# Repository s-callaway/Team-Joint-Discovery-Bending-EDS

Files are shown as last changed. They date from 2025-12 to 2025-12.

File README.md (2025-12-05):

# Team-Joint-Discovery-Bending-EDS
Repository containing all of the relevant information for Team Joint Discovery's senior design project

## ESP Motor Controller
The file containing "ESP32_motor_controller.ino" is to be used with an ESP32 and A4988 stepper motor driver. The limit switches are not required but are highly encouraged. If limit switches are not used, ensure that homing is defined to be false.

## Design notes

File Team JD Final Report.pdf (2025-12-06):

Team Joint Discovery

Bending Rig for an Electrodynamic Lunar Dust Shielding System

Final Report

ME 4723 – Interdisciplinary Capstone

Dr. Julie Linsey

julie.linsey@me.gatech.edu

Georgia Institute of Technology

Atlanta, GA

Drew Peljovich – ME

Jackson Buley – ME

Sasha Callaway – ECE

Spencer Hopkins – ME

Vikas Muralidharan – MSE

December 5, 2025

i

### Table of Contents

Appendix | A
Budget Appendix | C

ii

### Executive Summary

Lunar dust poses one of the greatest engineering challenges for sustained human presence on the Moon.

Its abrasive, electrostatically charged particles adhere to nearly every surface, degrading materials and

shortening the lifespan of critical systems. To address this, Team Joint Discovery was tasked with

designing a compact, vacuum‑compatible rig to test the bending performance of a flexible

Electrodynamic Dust Shield (EDS) thin‑film, a promising technology for dust mitigation in future lunar

missions.

The design problem centers on creating a repeatable, reliable bending mechanism that operates within the

strict constraints of Georgia Tech’s high‑vacuum chamber. Key technical hurdles include the chamber’s

limited size (6.1‑inch sphere with a 1×1 inch mounting platform) and the need for materials that can

withstand 10⁻⁸ torr without outgassing. The team’s solution leverages one existing and one purchased

linear bellows drive to cyclically bend the EDS film.

The team created structured design tools including a House of Quality, specification sheets, function trees,

morph charts, and evaluation matrices to guide the final product. The team translated stakeholder needs

into measurable engineering requirements. Market research and interviews with GT CLEVER researchers

and space technology experts further shaped the design, ensuring alignment with both research goals and

broader commercialization potential.

The rig’s key performance specifications include compact integration within the chamber, repeatable

bending cycles, and the ability to activate EDS during testing. Proof of concept was demonstrated by

successful cyclic bending of the EDS film in atmospheric conditions. This capability not only validates

the EDS under mechanical stress but also supports its potential use in protecting spacecraft components,

habitats, and instruments in lunar environments.

The final design is outlined in engineering drawings. Next steps for the project before implementation

under high vacuum is to translate these drawings and prototypes made of PLA material into machined

aluminum stock. Additionally, a motorized linear actuator will need to be purchased that is ultra-high

vacuum compatible to perform the bending test itself.

iii

### Nomenclature

Symbol | Meaning
Hz | Frequency, measured in Hertz
V | Voltage, measure in volts
Torr | Pressure, measured in torr

### Glossary

Acronym | Meaning
ASA | American Standards Association
ASTM | American Society for Testing and Materials
EDS | Electro-Dynamic Shielding
EVA | Extravehicular Activity
HOQ | House of Quality
IEC | International Electrotechnical Commission
JD | Joint Discovery

### Introduction

Team Joint Discovery has been tasked with developing a testing rig to repeatably bend a flexible

Electrodynamic Dust Shielding (EDS) thin film in a vacuum chamber. The film is made of a polyethylene

substrate with graphene-oxide channels etched into the substrate to form a conductive electrical grid.

When an alternating current (AC) of low frequency (10 Hz) and high voltage (>600 V) is applied to the

ends of the electrode, the EDS system is “active”, which repels dust from its surface. A visualization is

shown below in figure 1. Typical EDS devices include conducting electrode thin-films (Indium-Tin

Oxide, silver nanowires, etc). The application of these thin films is to attach surfaces that will face

performance issues due to dust collections such as solar panels and thermal radiators. Due to the material

composition of this specific EDS, it can bend and fold around surfaces as opposed to traditional inflexible

designs. This makes it particularly useful for a variety of lunar applications. Possible applications of this

system include shielding retractable/extendable spacecraft components, rovers, astronaut spacesuits from

excessive lunar dust, and on the outside of inflatable lunar habitats to protect from lunar dust kicked up by

human activity nearby.

A testing rig for the EDS system must comply with a set of strict problem

constraints for use in a high vacuum chamber. For one, the vacuum chamber

reaches pressures of 10⁻⁸
torr. As such, any equipment inside the chamber must

be able to withstand the pressure without collapsing in the high vacuum

environment. Additionally, some plastic materials cannot be used in the chamber

due to the off-gassing effects that could negatively affect the efficiency of the

closed system. Moreover, the vacuum chamber has limited mechanical

passthrough and electrical connection availability. The laboratory currently has

one linear bellows drive available for use in the vacuum chamber, and due to the

high cost of such devices it is preferrable to use the in-stock device without

purchasing other systems. There are six electrical connections available, but

under operating conditions with the dust dropper functioning and the EDS

powered, there are only two connections available.

Most importantly, the dimensions of the vacuum chamber present physical

constraints that will significantly impact the design of any internal mechanisms. The central sphere of the

chamber measures 6.1 inches in diameter. Within the central sphere sits a lunar dust hopper mounted to

the top of the chamber (see Figure 1). For mounting purposes, there is a 1inch-by-1inch platform to

Figure 1: Visualization
of EDS device secure the bending rig that will attach to the bottom of the chamber. The testing rig that will be used with

the EDS will have to conform to these size constraints, potentially sacrificing the ability to perform

different types of bending tests with one system.

The desired solution is a compact, vacuum-compatible bending rig capable of repeatable cyclic loading of

the EDS film. Key performance aspects include precise control of bending angle, durability under

vacuum, and integration with the dust hopper system. Proof of concept will be demonstrated by operating

the rig in the chamber with the EDS powered and dust applied, validating dust-repelling performance

under mechanical stress.

Value Statements

Scientific Impact: The proposed testing rig will enable scientists to repeatedly test the Electro-Dynamic

Shielding (EDS) system under realistic bending and dusting conditions, supporting validation of its dust-

repelling capabilities under cyclic loading.

Engineering Impact: The testing rig proposed also improves materials engineering testing in vacuum

conditions, forming design improvements and material selection for space-grade components.

Mission Reliability: Supports development of dust mitigation technologies for lunar rovers, astronaut

suits, and inflatable habitats, reducing downtime and maintenance in harsh lunar environments.

Commercialization Potential: Facilitates proof-of-concept demonstrations that can accelerate

technology readiness levels (TRLs), attract funding, and support patent filings for novel dust mitigation

systems.

This report covers Team JD’s initial problem brainstorming, including an analysis of existing products

(testing standards, patents), analysis of codes and standards, talking with stakeholders to identify their

needs, and the team’s initial designs.

### Existing Products and Prior Art

This section analyzes the current state of the art in lunar dust mitigation, with a focus on Electrodynamic

Dust Shield (EDS) technology. It identifies the gap in the market for a validated, flexible EDS system and

situates the test fixture and experiment plan within this landscape.

Several other dust mitigation strategies have been proposed or tested, but all have significant drawbacks

compared to the EDS. (Gaier, 2007)

Table 1: Existing Lunar Dust Mitigation Strategies/Solutions

Solution | Lunar Dust Mitigation Method | Pros | Cons
Mechanical Wiper/Brush | Physically sweeps dust off a surface | Simple mechanical design, potentially more deterministic | Moving parts than can fail due to presence of lunar dust; movement requires additional mass, power, complexity; ineffective for complex geometries
Compressed Gas Jets | Blows dust via a burst of gas | Simple solution with few moving parts | Consumable resource that is mass intensive; can further contaminate environment with dust redistribution
Passive Coatings | Superhydrophobic or other low-adhesive surfaces to reduce dust attraction | Solid state and simple solution | Not active; can wear down overtime with excessive use; cannot remove accumulated dust

The listed non-EDS solutions establish the clear need for a flexible, solid state, low power, and non-

consumable active cleaning system. This leads to the currently available and existing designs for EDS

systems for lunar dust mitigation.

Patent Search and Related Concepts

A preliminary patent search reveals significant activity in EDS technology, held by Boeing and Boston

University.

a. US12121910B2: “Dust mitigation system utilizing conductive fibers” (Boeing Co.). This patent

describes a flexible fabric like a dust mitigation system. This specific patent does not describe

bending evaluation/performance. It also is focused on using it as a woven fabric which is different

from the solution proposed by the GT CLEVER team.

b. US9433336B2: “Self-cleaning solar panels and concentrators with transparent electrodynamic

screens” (Boston University). This solution is for a firm EDS used to protect solar panels while

still allowing them to harness the sun’s radiation for power. The physical principle of dust

removal remains the same as GT CLEVER’s EDS, but it is not flexible.

The existence of these patents confirms the commercial and scientific value of flexible EDS. This project

does not seek to invent the flexible EDS itself, but to create the critical bending test required to mature

this technology.

A further example of prior art that was found comes from IPC Test Method 2.4.3, which depicts a test set

up that is designed to measure the bending performance of flexible printed circuit boards (Technical

Committees of IPC, 2022). This prior art demonstrates a proven methodology for testing the mechanical

durability of flexible, conductive materials, providing a foundational reference for the EDS-specific test

design.

Relevance and Differentiation for Intended Design

The test fixture and bending experiments are relevant to the prior art as stated before but is still distinct to

be its own project. The focus of this project is to quantify the EDS’ bending as a commercial selling point.

The test fixture will generate the quantitative data (e.g., "cleaning efficiency remains >95% after 1,000

bend cycles to a 5mm radius") required to substantiate this advantage to potential customers like NASA.

There exists no commercial "Flexible EDS Bending Test Fixtures" on the market. The design addresses a

specific, unmet need within the R&D pipeline for this emerging technology.

Existing Testing Systems

There are very few existing test systems that allow cyclic bending of a flexible film inside a vacuum

chamber, particularly in laboratory-scale vacuum systems. Most vacuum test fixtures focus on thermal

cycling, outgassing characterization, or static mechanical loading, not repeated flexing of thin-film

electronics. Because of this, the closest prior art comes from adjacent domains that required similar

mechanical-in-vacuum capabilities.

One of the most relevant examples is a NASA study titled “The Effect of Vacuum on the Fatigue and

Stress-Rupture Properties of S-816 and Inconel 550 at 1500°F.” (Freche, 1965). Although the study

investigated high-temperature fatigue in metallic specimens rather than polymeric films, the mechanical

test architecture is directly applicable to the requirements of a flexible EDS evaluation.

Figure 2: Fatigue Test Apparatus

Although the mechanical scale and material system differ from the thin-film EDS, this NASA apparatus

demonstrates that cyclic bending in vacuum can be achieved using external actuation and vacuum-

mechanical interfaces. The NASA fatigue apparatus serves as architectural precedent but fails to provide

the specific integration of vacuum operation, controlled bending radius, and electrical excitation needed

for flexible EDS validation.

### Codes and Standards

Several codes and standards informed the ideation of the first prototype. Included in this section is a

summary of those codes and their relative importance.

IEC 62899-202-5

IEC standard 62899-202-5 is the most applicable to team JD’s final product. An excerpt from the

introduction highlights the basis for the reason behind this application:

In this document, a mechanical bending test is described to evaluate the electrical property of a printed

conductive layer on a substrate under repeated mechanical deformations. This sliding plate test method

can be available for practical application in the industry by enabling the long-term reliability testing of

printed film. (TC 119 - Printed Electronics, 2018)

The EDS system is very similar to the film described in the standard. A graphene layer is printed on top of

a polymer substrate to repel the lunar dust. Furthermore, it is necessary to repeatedly deform the piece to

understand its resilience to bending. The standard gives clear instructions on how to perform the test, and

the structure of the bending rig itself. When comparing team JD’s ideation to Figure 3, the IEC standard

served as a clear inspiration for the final design.

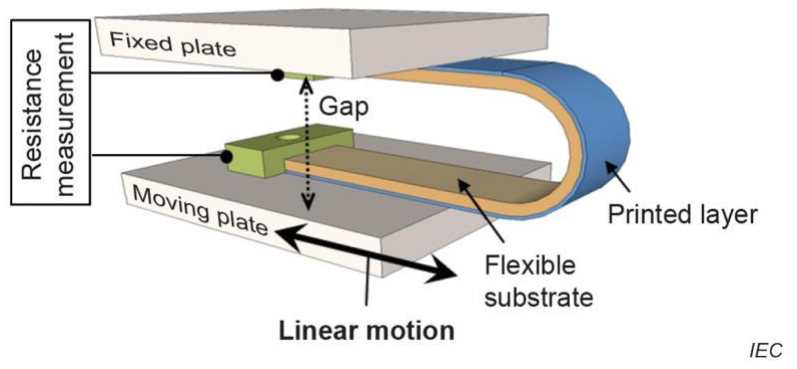
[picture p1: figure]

Figure 3: Schematic diagram of mechanical test of printed film

While not explicitly described, the standard does call out for variable adjustment of the gap between fixed

and moving plates. Team JD will implement this variability in the final design, but not follow the exact

mechanisms described in the standard. The test depicts the horizontal motion of the printed layer by the

moving plate. After speaking with key stakeholders, this will not be possible in the final design.

Therefore, Team JD will have to modify the standard so that it can perform in a vertical position.

Other Applicable Standards

During the ideation phase of the project, Team Joint Discovery found and used several other standards as

a basis for the final project. While not implemented as directly as 62899-202-5, these standards guided the

team towards the end goal and provided inspiration for certain design choices.

The first of the standards considered was ASTM

F392, called Standard Practice for Conditioning

Flexible Barrier Materials for Flex Durability. This

standard describes a torsional test of flexible

packaging material used in food packaging and

shipping. Originally, Team JD considered the

possibility of a torsional rotation test performed in

the vacuum chamber. This standard was extremely

useful to help ideate this application and described

the specifics of conducting such a test. The benefit

of this standard over others was the mechanics of torsion helped simulate a new variety of loading

conditions for EDS. Torsional tests better simulate end uses of EDS such as twisting limbs on a spacesuit.

However, after consulting key stakeholders and understanding of the project, the spacesuit end case of

EDS was determined to be less feasible than the other uses of EDS. As such, this standard was not

directly adhered to in favor of other testing methods.

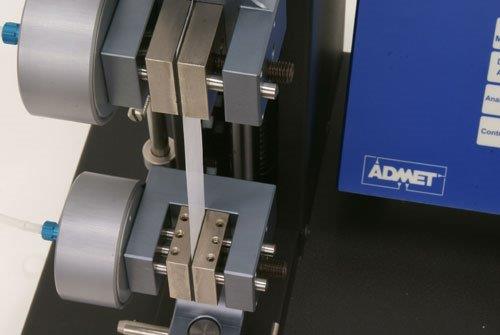
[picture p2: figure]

Additionally, another type of testing not pursued by

team Joint Discovery was detailed in ASTM D882

titled: Standard Test Method for Tensile Properties

of Thin Plastic Sheeting. This standard outlines the

procedure for conducting a single plane tensile test.

The purpose is to measure the film’s modulus of

elasticity and compare the stiffness to theoretical

results. This test would have simulated an

extendible spacecraft part or other actuating

equipment. However, conducting a tension test in

the vacuum chamber with preexisting linear actuators is a trivial task. While the overall test was not

selected to govern the final design, Team JD did take inspiration from the clamping mechanism for the

test. One of the challenges in the final design of the overall system was how to clamp the EDS to the

mounting plate. Using inspiration from this test on the clamping mechanism for the EDS was very

valuable in the final design in understanding how to hold a thin plastic film.

Figure 4: ASTM F392 Torsional Test

Figure 5: ASTM D882 Tension Test

Furthermore, two standards related to flexible devices were investigated. First ASTM F1683: Standard

test method for folding endurance of flexible

organic light-emitting diode (OLED) devices.

The beauty of this test is that its purpose is to

roll and bend a film over and over again. The

standard offers a fairly simple test to study

bending, but the team did notice that a large

amount of material would be needed to

effectively test the EDS.

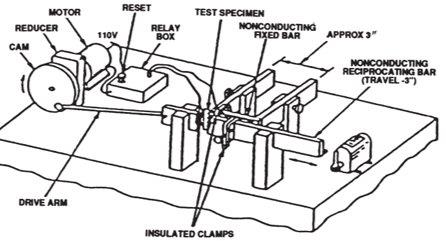
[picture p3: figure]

A result of the small sample size meant that

this standard could not be faithfully used, but

the simplicity in design was something the

team carried forward. Lastly, the time also

investigated IPC-TM-650: Testing method for

repeated bending of flexible printed circuit

boards. The motivation to look into this

standard was that it closely resembled the EDS

device: a flexible printed film. The team

dubbed this test a “piston test” as there was a

rotating CAM that enabled the repeated bending of a test specimen. In this device, there is a standard

spacing between ends of the flexible PCB design, which the team thought was limitation for the EDS.

The positive idea of this standard is the ability to impart motion from a distance from the sample. This

idea was taken as inspiration during the concept generation and prototyping phase.

Figure 7: IPC-TM-650

Figure 6: ASTM F1683 Visualization

Ultra-High Vacuum Standards

Any mechanical part in use in the ultra-high vacuum

chamber must be specifically designed for the extremely

low-pressure environment. This includes complying

with the standardized American Standards Association

(ASA) flanges and fittings. These allow for mechanical

and electrical passthroughs to be fed directly into the

chamber during use and create a leak-tight seal

preventing failure. The testing rig that is being designed

must comply with these standard flanges. As seen in

later designs, the use of a linear actuator is paramount to

the final design’s success. This linear actuator is a

vacuum standard part and complies with the ASA

flanges. Any additional parts will also have to be

standard and purchased from a verified vendor that

supplies these types of parts, such as the Kurt J. Lesker

company.

Furthermore, any part in use inside the vacuum chamber must be designated vacuum chamber compatible.

This is a specific designation that is different than outer space vacuum compatible. These vacuum

chamber parts have to be designed to minimize outgassing effects, where small contaminations can ruin

the experiment being conducted in the closed chamber environment. To get the designation, only very

specific equipment can be used, which could potentially drive up the costs of the final product. The team

will have to design the final product very carefully to account for these parts and take note of their

associated costs.

Figure 8: Side view of Vacuum Chamber with ASA Standard Flanges

### Customer Requirements

This section will analyze the customer requirements and how these translate into engineering

specifications. Included is a stakeholder chart, list of customer requirements, engineering design

specifications, and finally a house of quality.

Stakeholder Analysis

The stakeholders are specific personnel that team Joint Discovery actively engages and collaborated with

in pursuit of the project goals. Table 2: Stakeholder Matrix shows all of the stakeholders and their relative

importance/influence on the project.

Table 2: Stakeholder Matrix

Stakeholder | Interests | Importance | Influence
Dr. Linsey (sponsor) | Ensure delivery of working prototype and adherence to ME guidelines | High | High
Luca and Ide (Grad Students) | Oversee the project and give vital feedback on our designs. Understand the end goal and can steer us in correct direction. | High | High
Dr. Alvoro Romero-Calva (AE Professor) | Has expertise on the companies and the end-use for the EDS system, can give guidance on proper tests to conduct on the system. | Medium | High
Dr. Orlando | Oversees the lab and the grants given to GT clever to conduct this research. Knowledge of available parts and mechanisms to use. | Medium | Low
NASA | Provides the money to GT clever to develop the EDS testing rig. Financial interest in the project's success. | Medium | Low
Space Companies | The end user of the EDS product, will purchase the system to apply to space missions in the future and will want data quantifying its performance. | Low | Medium
Dr. Meisha Sofner (MSE Professor) | Has expertise on thin films and can give guidance on proper testing procedures and techniques. | Low | Medium

Communication with high importance stakeholders is conducted on a weekly basis at minimum. These

are conducted through in person meetings and frequent online messages. This is done to ensure the team

stays closely aligned with the project’s end goals, with constant collaboration necessary to steer the team

to the same direction envisioned by the project sponsor and grad students.

Additionally, while not directly tied to the success of the project, stakeholders such as Dr. Romero-Calva

and Dr. Meisha Shofner are great resources to understand the project specifics and gain feedback on

certain unknowns during the ideation phase. Finally, NASA and other space companies are interested

parties in the product. Since they are interested in using the EDS system on future lunar missions, getting

data on efficiency while bending is critical. These stakeholders are less involved in the ideation and

prototyping phases of the project, but critical in the product. Their needs and requirements are fed through

the other stakeholders and ultimately guide team Joint Discovery’s process through the capstone semester.

Customer Requirements and Functionality

While the EDS system works well in a well-controlled environment, the team behind its development has

little data on the lunar repulsion in states of bending. Therefore, the main requirement for the project

was the development of a bending rig that could perform bending to the EDS system while in the

vacuum chamber. However, no specific test or degree of bending was required, only that the bending rig

should be able to give quantifiable data to researchers to understand how the EDS works.

The EDS system as a whole needs to be marketed as a reliable and dependable system. Without hard data

showing its efficiency in different loading conditions, the team at GT clever cannot sell the device for use

on the moon. As such, another overarching requirement is to gain usable and impactful data from

the bending rig. This requirement is also kept vague as to not constrain the types of tests that team JD

might want to run. The purpose of this requirement is to remind the team that at the end of the capstone

semester; the stakeholders are looking for data to substantiate their claims about the EDS system. There is

no measure of “how well” this can be accomplished, only that any data is better than none.

Lastly, because of the vagueness of the problem, there is a need to relate the bending tests to something

more standardized. This way, when presenting the results of a bending test to an end user, the data can be

related back to a regulated standard to help explain what they mean. Consequently, the testing rig must

be closely alighted with an ASTM or food safety standard. The specific standard is left vague, again as

to not constrain which types of bending tests can be performed. However, alignment with at least one

standard is paramount so that the system and its results can be understood much easier.

### Engineering Design Specifications

This section of the report will discuss the specifications for the engineering design of the final product.

Included will be an analysis of the constraints and a specification checklist that will inform a House of

Quality that summarizes the overall tolerances and requirements for the project with specific tolerances

included.

Engineering Constraints

Despite the open-endedness of the problem, there are still many constraints for the project. First, the

system must work inside an ultra-high rated vacuum chamber. This poses a series of connected

requirements for the overall design: the physical size of the chamber, material selection, and availability

of feedthroughs. Additionally, the chamber uses standard feedthrough windows that any purchased part

must be compatible with. The high-rated vacuum also poses specific material constraints. Plastics and

other polymers have severe off-gassing properties that could cause damage to the system. As such, only

metals and other vacuum-rated parts can be used inside of the chamber during operation.

Engineering Design Specifications

Based on the customer requirements, engineering functionality, and constraints for the project, team Joint

Discovery has created a robust set of engineering design specifications that will encompass the project

scope. As seen in Table 3: Engineering Design Specifications List, the team has developed 5 main

categories of requirements: General, Physical Characteristics, Electrical, Mechanical, and Performance.

Table 3: Engineering Design Specifications List

| | Issued: 9/23/2025
| | For: Team Joint Discovery
| | Specification
Date | D/W | Requirements | Source/Rationale | How Validated

General

23-Sep | D | Perform bending on the EDS system up to 180 degrees | Perform full bending test of EDS | Observe Final Design
23-Sep | W | Bend the test piece while electronics are powered and lunar dust is dropped on top | Give data to researchers about the functionality of EDS during bending | Observe Final Design

23-Sep | D | Allow for camera view of film during dusting + flexing | necessary for measuring performance of film | Observe Final Design
29-Sep | D | The testing rig is not to obstruct the dust deposition from the shaker | The test specimen must continue to be dusted while bent | Observe Final Design
23-Sep | W | Allow for variable radius of bending | Give data correlating radius of bending versus the effectiveness of EDS | Observe Final Design

Physical Characteristics

23-Sep | D | Must fit inside the vacuum chamber (<155 mm diameter) | Provided by Luca Scifoni | Measure final design overall size
23-Sep | D | Must be capable of mounting within vacuum chamber | Provided by Luca Scifoni | Observe final design
29-Sep | D | Compatible with 2"x1.5" films for 2-phase configuration | Provided by Ide Onal | Measure final design overall size
29-Sep | W | Compatible with 3"x2" films for 3-phase configuration | Provided by Ide Onal | Measure final design overall size
23-Sep | D | Materials used must be high-vacuum rated (10^-8 torr) | Provided by Luca Scifoni | Select materials that withstand this pressure

Electrical

29-Sep | D | Use Kapton insulated wire for all harnessing internal to chamber | Provided by Luca Scifoni | Observation
29-Sep | W | Use vacuum rated linear actuators | Provided by Luca Scifoni | Material selection

Mechanical

23-Sep W

Limited to use of lab provided

linear actuator as mechanical

feedthrough

Due to limited funds, not

requiring the purchase of

additional high-vacuum

parts would be beneficial for

the final design

Observe final

design

1-Oct W

Build in a heat dissipation method

to cool motors during operation

Due to the small enclosed

space, heat can rapidly build

up in the chamber and

affect the operation of

internal equipment. Need a

way to control the

environment temperature

during experiment

Heat Transfer

Sensors

Performance

23-Sep | W | Bendable for 1000 cycles before failure | Provided by Ide Onal | Run fatigue life calculations on testing rig to ensure product lifespan
29-Sep | W | Adhere to IEC 62899-202-5 testing standard | Provided by Dr. Orlando, standard selected is most similar to EDS applications | Compare final design to testing standard

The general category describes the overall functionality of the bending rig. Bending the test piece a full

180 degrees while allowing for dust to drop on top of the polymer in view of the camera is a critical

functionality of the testing rig. Failure to comply with these requirements would result in unusable

equipment for the purposes of the project.

The physical and electrical characteristic requirements describe barriers for the system in real space. They

dictate the maximum size allowable in the chamber, compatibility with test pieces, and availability of

electrical connections. These physical requirements, while not explicitly related to the end goal, are

critically important and stem direction from the problem understanding.

The mechanical and performance categories dictate the practical applications of the bending rig. They

explain how the system needs to function and give requirements for the ways that the bending can be

induced.

Importance of Specifications (House of Quality)

Together, the constraints and requirements can be summarized into a house of quality showcasing the

importance of each task. The HOQ lists the customer requirements and engineering requirements, giving

the specific tolerances and target values as well.

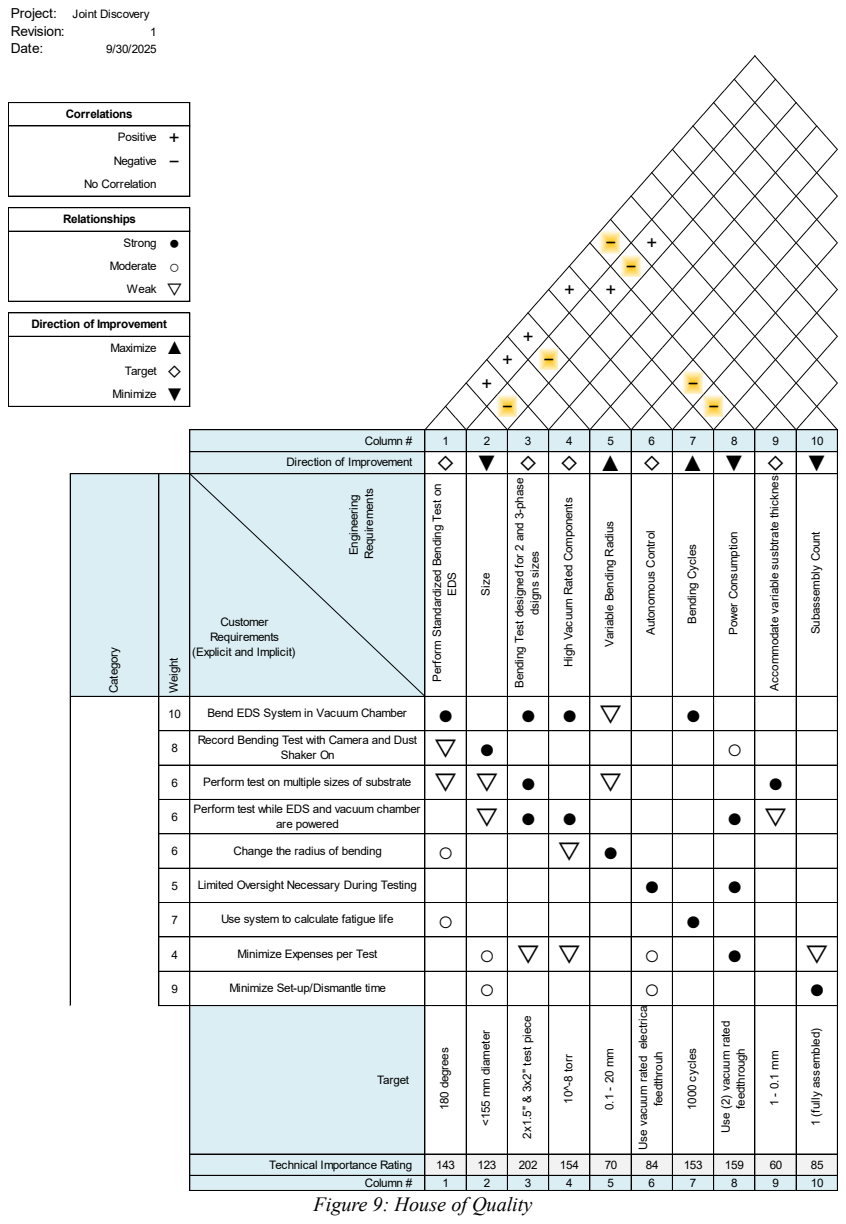
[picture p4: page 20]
Project:; Joint Discovery; Revision:; Date:; Engineering Requirements; Column #; 180 degrees; <155 mm diameter; 2x1.5" & ³x2" test piece; 10^⁻8 torr; Use vacuum rated electrical; feedthrouh; 1000 cycles 1◇; Maximize; Target; Minimize; Correlations; Positive +; Negative −; No Correlation; Relationships; Strong ●; Moderate ○; Weak ▽; Figure

1086665749 Weight | Minimize Set-up/Dismantle time Limited Oversight Necessary During Testing Customer Requirements (Explicit and Implicit) | | + +− ▽ ● Size | ▽ ● ○● ● Bending Test designed for 2 and 3⁻phase dsigns sizes | ▽ ● High Vacuum Rated Components | + − − + ● Variable Bending Radius | + ● ○ ○ Autonomous Control | − − − + Bending Cycles ○ | ○ ● ● ● ○ ● Power Consumption | ▽ ▽ ● ▽ Accommodate variable susbtrate thickness Perform Standardized Bending Test on EDS | Subassembly Count ◇ ▽ ○ ●▼ Category

Direction of Improvement

Bend EDS System in Vacuum Chamber | | | | | ▽

Record Bending Test with Camera and Dust Shaker On

Perform test on multiple sizes of substrate | ▽ | ▽ | ● | | ▽

Perform test while EDS and vacuum chamber are powered

Change the radius of bending

Use system to calculate fatigue life

Minimize Expenses per Test

Target | 143 | 123 | 202 | 154 | 70 | 84 | 153 | 159 | 60 Use ⁽2⁾ vacuum rated feedthrough 1 ⁻ 0.1 mm | 1 ⁽fully assembled⁾

Technical Importance Rating | | 2 | 3 | 4 | 5 | 6 | 7 | | | 85 1

9: House of Quality

After gathering the customer requirements from key stakeholders, the most important customer

requirement is bending the EDS system in the vacuum chamber. This tracks from the overall goal of the

project, and serves as a reminder for the team to stay unified in completing this shared goal. Furthermore,

it can be sold off by a variety of engineering requirements and their target values: performing

standardized bending test on the EDS (180 degrees), bending designed for 2 and 3 phase sizes (2x1.5”

and 3x2”), high-rated vacuum components (10^-8 torr), and number of bending cycles (1000). Designing

a testing rig that can accomplish all of these engineering requirements will satisfy the customer’s needs

and be marked as a successful project.

The second most important requirement was not as obvious to the team at first. That is minimizing the

set-up and dismantle time. Direct cost is not a critical requirement in this project (listed with weight 4) as

the price to run the vacuum chamber and purchase the materials is low. The true cost is associated with

the grad student’s salaries and available time to work on the project. Since they have other tasks and work

to complete as part of their schooling, minimizing the time needed for them to actively work with the

testing rig is a key requirement. This will indirectly drive down the costs of the system and allow for other

work on the EDS system to be completed. Set-up time is directly tied to the subassembly count, meaning

the team is trying to create a fully assembled testing rig that would minimize the time needed to set up.

Subsequently, recording the bending test with the camera on is the third customer requirement listed for

the project. The camera is the only way to quantify the amount of dust being repelled by EDS, and so

recording the experiment is paramount for the team. This is strongly tied to the testing rig’s overall size

and positioning in the chamber. At its diameter, the vacuum chamber measures 155 mm. Additionally, the

top area is dominated by the lunar dust dropping mechanism. Available space for the testing rig is tight,

and positioning the rig so that it is viewable from the camera will be a challenge. However, failure to

accomplish this task will starve the researchers from gaining useful information about the EDS behavior

in bending applications.

The other customer requirements, while not weighed as high, are still useful to team JD in understanding

the project goal. They are translated into engineering requirements that shape the final product and help

focus the capstone team into achieving these goals.

### Market Research

This project’s market research and potential impact scope can be understood through two different lenses:

as a product for GT CLEVER’s EDS research team, and another for the EDS as a product for space

agencies and commercial organizations. For the former, the focus is providing a solution to the research

team to demonstrate and evaluate their EDS’s bending performance. For the latter, the market and impact

are significantly larger and not as hyper specifically concentrated on a certain client.

Market Research Plan

The market research plan for the GT CLEVER research group will consist of meeting and interviewing

people directly involved with the EDS team. The graduate students working on the project will provide

Team JD with hands-on knowledge of constraints and customer needs. Specifically, Luca Scifoni is the

aerospace engineering PhD student who works directly with the vacuum chambers that the EDS is tested

in. The specific mechanical and environmental constraints of the vacuum chamber are central to the

problem and the information garnered from talking with Luca will be invaluable. From the material

science perspective of the problem, Ide Onal is the material science and engineering PhD student who

will provide the necessary information for the evaluation of the EDS’s bending characteristics. Dr. Julie

Linsey is the resource for general questions regarding the scope and performance of the project.

From the perspective of the EDS as a commercial product for space related organizations, Dr. Romero

Calvo, director of Georgia Tech’s Low-Gravity Science and Technology Laboratory (LGST Lab), will be

the main point of contact for interviews and questions regarding the market and potential impact. Further

resources will come from publicly available space organizations for documents and plans. This

specifically includes NASA roadmaps and Artemis mission plans.

Market Research Results

The interviews and discussions with Dr. Linsey and the graduate students working with GT CLEVER

provided important context for the design of Team JD’s product but also insight into the market. The

market for the specific device that GT CLEVER would use to evaluate their EDS is constrained to just the

GT CLEVER organization. Therefore, it is quite limited in terms of commercial viability. There is a

potential to sell this product to other research or commercial organizations who develop their own version

of a flexible EDS and would like to test their device to the same standards as the ones done by the GT

CLEVER team. If validating GT CLEVER’s EDS bending performance using the aforementioned

standard and test fixture becomes the industry accepted way to test such shields, it would create a market

for commercial and research organizations seeking to buy or license the technology. This market would be significantly smaller than that of flexible EDS as it would likely be a one-off purchase for the company

or research organization to validate their design.

From the commercial side of this project, market research is more tangible. The first part of this is

understanding where the EDS could potentially be used, as it is not designed for a hyper specific use case

now. A significant part of the discussions with Dr. Calvo and research focused on potential applications.

These include but are not limited to shielding spacecraft components and actuators, instruments such as

cameras, extravehicular activity (EVA) suits, and habitat modules. Dr. Calvo expressed significant doubt

of EDS working with EVA suits due to the human factors risk associated with high voltages on the outside

of the suits. The other applications, however, leave a lot of room in the market for EDS. This section of

the report will briefly focus on the market of EDS from two lenses: mass saved due to EDS protection,

and the mass saved due to picking flexible EDS over another lunar dust mitigator. Astrobotic is a lunar

services company which provides numbers for soft landings on the lunar surface (Astrobotic Payload

Management, 2021). Using their provided value of $1.2 million dollars per kilogram, the EDS can create

vast market value just from mass savings alone. It is hard to put specific numbers now due to the early

stage of EDS development, but if an EDS can protect or increase the lifespan of just 10kg of sensitive

lunar infrastructure (instruments, hatches, actuators, etc), EDS has provided a value of $12 million in just

delivery costs, let alone the savings from not having to purchase the replacement infrastructure and the

losses caused by its downtime. This calculus can further be used to demonstrate the mass savings by using

extremely light weight and low power EDS as opposed to other lunar dust mitigation strategies such as

mechanically actuated metal brushes and cold gas thrusters (Tatom, 1967). For full scale Artemis

missions, the potential mass savings impact of the lightweight EDS could be on the order of hundreds of

millions of dollars. Further, the EDS is a solid-state system, requiring no additional mass to function (such

as cold gas thrusters), relatively low power as opposed to mechanically actuated systems, and no moving

parts, so reliability is significantly higher.

Market Research Impact on Design

Important context for the design of this project to demonstrate the EDS’ bending performance as a

commercial selling point. Keeping this in mind, the market research learned has adjusted the specific

standards and tests that Team JD will use to demonstrate the EDS’ characteristics. Talking with the GT

CLEVER researchers who are directly involved with this project has significantly helped tailor the design

and strategy for this project, giving specific feedback and information that constrains the problem to

create an effective solution. Such specific feedback includes the environmental constraints given by the

vacuum chamber and the specific type of wiring and materials that must be used in high vacuum.

### Design Concept Ideation

Functions to be Filled by Design

The primary function of the design is to enact repeated stress tests on the EDS subject and analyze the

device’s performance in repelling artificial regolith after multiple cycles. At the highest level, this can be

split into 3 sub-functions: Induce Stress on the Substrate, Mount and endure testing within the chamber,

and produce validated and replicable results:

Figure 10: High Level Function Tree

Inducing stress on the EDS device can vary greatly in form depending on the standard adhered to.

However, all can be broken down into a mechanism to induce motion on the substrate coupled with a

mechanism to resist this motion. Both will be reliant on how the EDS is mounted within the rig as well.

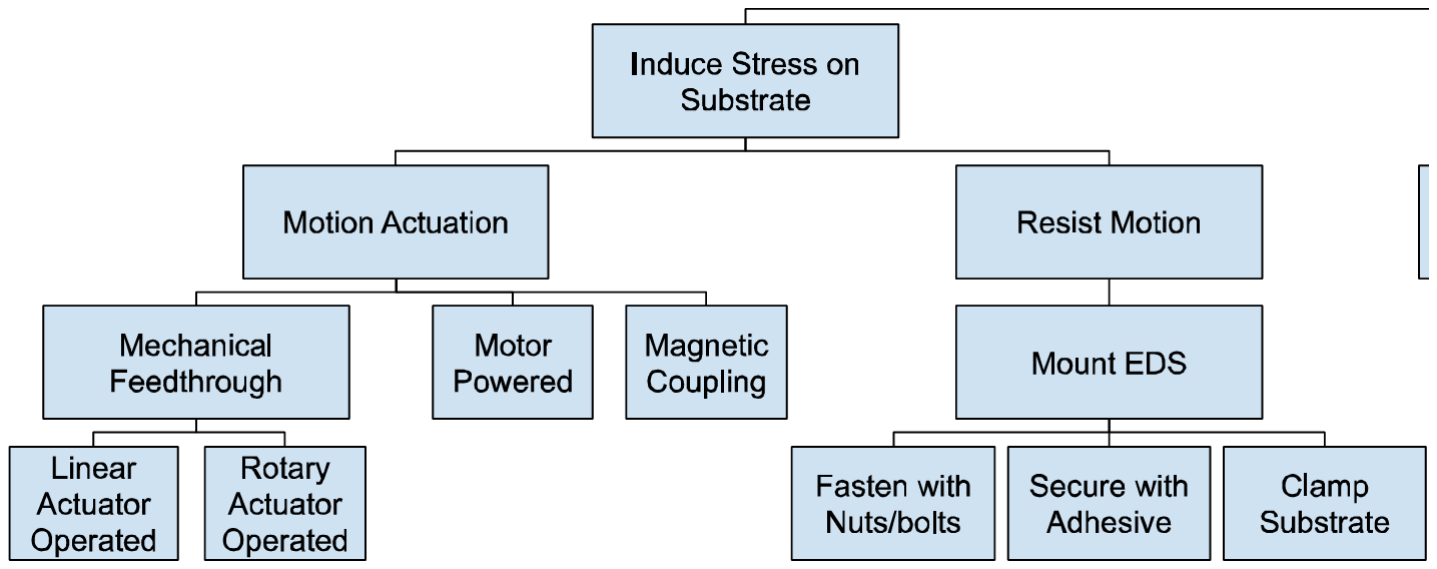
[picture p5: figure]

Figure 11: Function Tree Branch 1

To adequately perform stress tests, the design also must be mounted in the chamber while enduring the

optimal testing conditions – Vacuum rated conditions, power running through the EDS, and artificial regolith falling. Mounting within the chamber is constrained by the current equipment and the testing

environment.

Figure 12: Function Tree Branch 2

To endure this environment, the rig must be vacuum rated and be able to avoid suffering damage from

regolith wear. Regolith is a harsh substance which can create multiple failure modes in testing, and thus

the rig must be designed with countermeasures in mind. To avoid this damage, parts must either be

selected to be strong enough to not be worn down by it, have regolith continuously removed from them,

or not move when regolith is present.

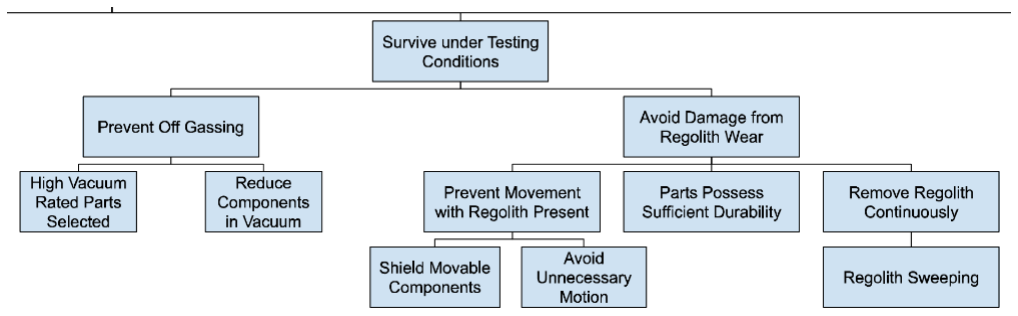
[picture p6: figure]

Figure 13: Function Tree Branch 3

Lastly, even if the testing is performed, it is not relevant unless it provides meaningful and replicable

results. As such, it must adhere to a relevant testing standard and perform meaningful data collection. To

determine meaningful data collection, there also must be established criteria for success or result

validation. Team Joint Discovery has devised multiple alternative solutions for these functions that define

the testing essentials, and the successful completion of them will provide a strong basis for a working

prototype.

Figure 14: Function Tree Branch Number 4

Alternative Solutions to Fulfill Functions

Inducing stress on the EDS involves a means of moving the substrate while providing resistance. Motion

can be provided via mechanical feedthroughs in the form of a linear or rotary actuator. Other options

include a magnetic coupling paired inside and outside of the chamber, or utilizing a vacuum rated motor

which only requires electrical feedthroughs, which are significantly more available. To resist motion, the

EDS can be held stationary by threaded fasteners as have been done in previous non-bending tests, a

vacuum rated adhesive, or a clamp to distribute the load.

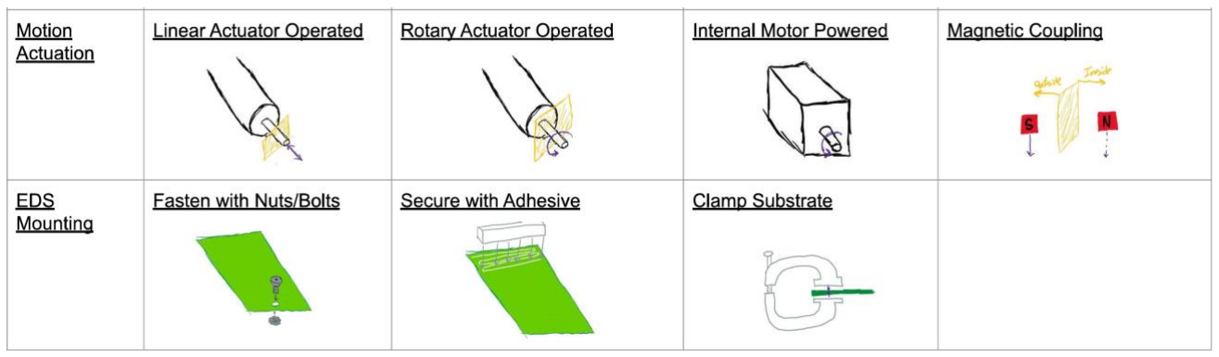
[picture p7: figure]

Figure 15: Morphological Chart - Motion Actuation and EDS Mounting Mechanisms

The mounting of the rig within the chamber can be done in a few different ways with varying stability,

cost, and reliability. One method is with Groove Grabbers, a part made by the manufacturers of the

vacuum chamber to be joined at the flanges and mount components inside. Another option is mounting

via magnetic coupling, and finally via a vacuum rated epoxy.

Figure 16: Morphological Chart - Test Rig Mounting Mechanisms

An additional critical aspect of the testing rig is being able to survive under specific testing conditions.

Primarily, they must be vacuum rated, have no off gassing, and be able to avoid damage from regolith

wear. Considered manners of avoiding regolith wear include selecting parts durable enough to avoid

frictional wear, preventing movement of parts near regolith, and removing the regolith continuously

before potential points of contact with a sweeping mechanism. Preventing movement of parts near

regolith can consist of shielding the movable components or replacing/eliminating motion altogether

where it is non-essential.

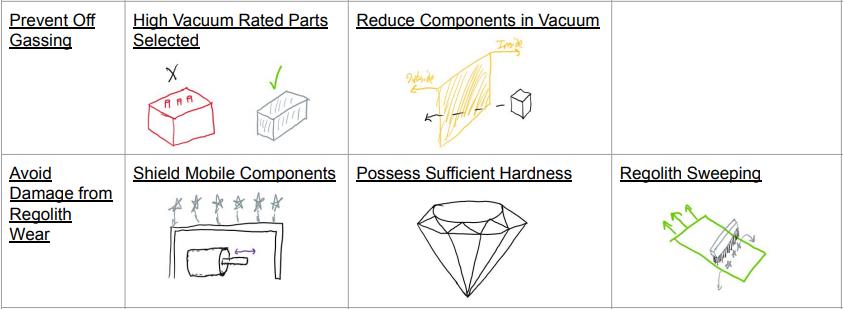
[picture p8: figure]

Figure 17: Morphological Chart - Mechanisms to Survive Testing Conditions

Finally, it is critical for the stress testing to produce meaningful data in a replicable manner by following a

relevant testing standard to provide a level of validity to the results, as well as being able to measure and

collect this data consistently. There were a wide range of ASTM and IEC standards examined for various

forms of stress testing and applications which are further examined as the basis of our integrated

concepts. Important subfunctions of data collection included establishing a method of assessing results

and include the current method of visual inspection via a camera and measuring the resistivity of the

circuit when stressed as discussed in ACS Appl. Polym. Mater. 2025, 7, 9211-9223. Additional essential components of testing involve providing power to the EDS through electrical wiring feedthroughs and

dusting the specimen to assess its repelling capabilities. This can be done by either bending the specimen

multiple times and then dusting it or dusting it as it is being bent. These solutions address the

subfunctions necessary to produce meaningful data that is desired by the end user.

Figure 18: Morphological Chart – Mechanisms to Collect Meaningful Data

Integrated Preliminary Designs

The most influential subfunction for ideation early on was

selecting a standard to adhere to. The various standards

examined served as our bases for design in our more fleshed

out and integrated concepts. These integrated concepts were

each centered around a standard while integrating different

versions of the previous subfunctions. Bending, tension, and

torsion are three ways to quantify the movement of the film,

but some applications of this EDS would have a combination

of two or three. Therefore, the team also considered more

generic tests for fabric folding emulation and a creasing

consideration.

Bending is a very likely mode to be encountered in

the EDS’ widespread potential applications. It can

be found in the movement of joints, both

mechanical (on curved surfaces and actuators), or

human, (on a spacesuit). Due to this wide range of

applications, multiple potential bending tests have

been developed with varying degrees of bending,

bending radii, and points of contact. One testing

method, inspired by ASTM E855, involves a 3 or

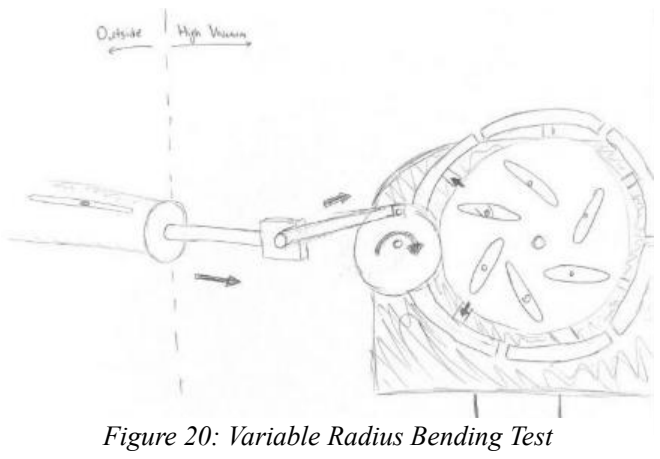
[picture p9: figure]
Figure 20: Variable Radius Bending Test

4-point bending test where a neutral substrate is prodded in

one or two locations to induce bending stress. Another uses a

slider-crank mechanism to convert linear motion to rotary,

rolling a mandrel (that can be variably sized) across the

static test piece to induce bending stress. Another standard

that the EDS could potentially be tested to is specified in

IPC-2223 and IPC-6013D, which establish standards for the

design and qualification/performance of flex and rigid flex

PCBs. These standards refer to the IPC-TM-650 Test

Methods Manual which specifies fatigue tests and fatigue

behavior for flex PCBs. ASTM F1683-96a provides a

bending standard that is most obviously applicable to this

Figure 19: ASTM E855 Based Bending Test

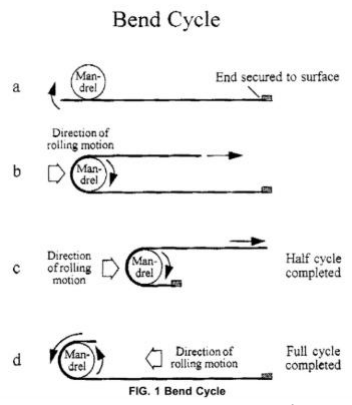
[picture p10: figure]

Figure 21: ASTM F1683-96a Bending Test testing, although it may not provide sufficient understanding of how the device operates under different

types of bending.

Tension is another primary flexing mode that could be useful for an application engineer to understand

before utilizing this film on their product. For example, if this film were used on an inflatable structure

(balloon-like), it would be vital to know

how much it can strain before lunar dust

mitigation is compromised. Therefore, a

linear tension test could provide

repeatable information for performance

as a function of stress or strain (likely

strain, considering the linear actuator

which is available). The drawback to this

test is it would not consider bending,

which could be a very important flexing

mode to understand when evaluating the

performance of these films.

Figure 22: Tensile/Bending Test

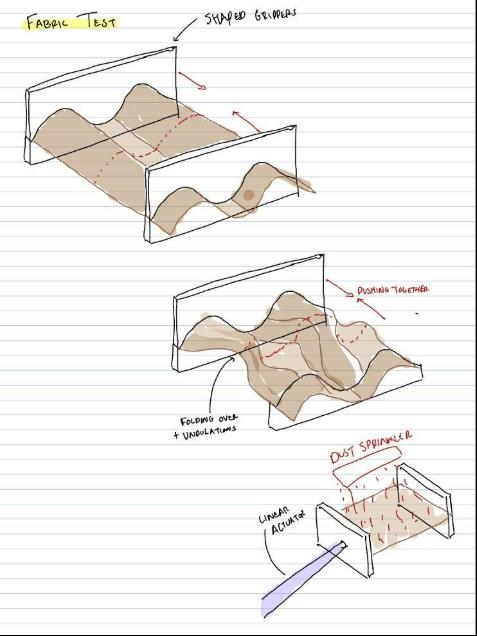
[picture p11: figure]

A general case for these flexible EDS’s is with

foldable, fabric-like surfaces including space suits

and inflatable habitats/satellites. If these are

intended uses, a test that demonstrates the ability

of the EDS to reject dust while folded or stored

akin to these cases would showcase the film’s

efficiency in these applications. For this reason,

the team is proposing a vacuum test that focuses

primarily on enforcing fabric-like folding

behavior. These tests would be qualitative in

nature, as it would be difficult to quantify the

number of wrinkles in a fabric. This test also has

the advantage of using only the linear actuator,

which would simplify the device. However, if the

primary goal of this project is to showcase the

film’s effectiveness under this specific use-case,

this demonstration would be the most effective

showcase of such. From the team’s discussion

with Dr. Linsey and Dr. Romero-Calvo, the

application of this device to spacesuits seems unlikely, and so this specific use-case does not seem like the

most important test to pursue.

Figure 23: Fabric Replication Test

### Concept Selection and Justification

There is a good understanding of what the system could test, but it is vital to properly define what testing

the setup should actually perform. There are many standards that could be tested, and the selection of

which design should be pursued is a combination of how well the appropriate standard applies to the

desired application and how feasible the device is to fabricate and meet the strict requirements on space

and vacuum rating. Going into the concept selection phase, three primary designs were considered, each

of which provides a different set of valuable information for how the films act under bending.

Design #1 is designed for the specific standard IEC-62899-202-5, and consists of a linear actuation that

repeatedly bends the film, with some sort of secondary adjustment to change the radius of the film. This

test meets a standard that very closely applies to the film being tested, and is feasible with the constraints

listed.

Figure 24: Sketch of Design #1

Design #2 is designed for the standard IPC-TM-650, which is the broader standard for flexible circuit

boards. There is some documentation online about a theoretical device used to test this standard, but not

any specific drawings or details.

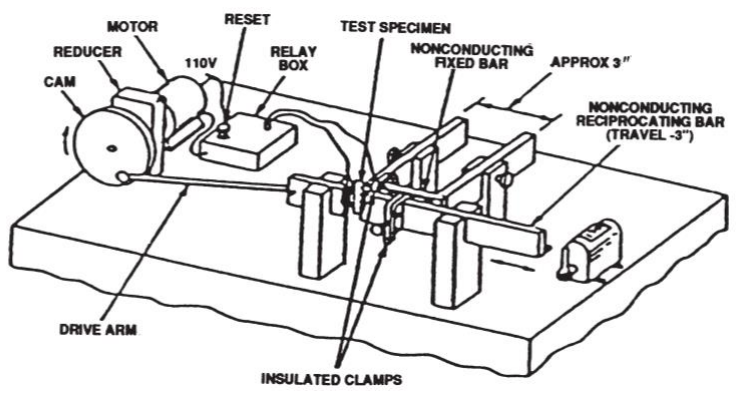
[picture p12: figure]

Figure 25: Drawing from standard, Design #2

Option #3 is a design that is not based in any standard, but could provide valuable insight into the film

under a larger variety of flexing tests. The tradeoff here is more freedom to test with the drawback of not

meeting a strict standard.

Figure 26: Sketch of Design #3

In order to adaquetly evaluate these designs, an evaluation matrix was made to compare how each idea

effectively meets the requirements. The most important criteria were that the film should adhere to a

standard, since this will provide the best data for effectively communicating to potential investors the true

capabilities of this device. As seen in Figure 21 Design #3 had significant hits in this category. However,

as expected, Design #3 shined in criteria that were focused more on versatility. Specifically, #3 scored

highest in the testability while being viewed with the camera and unobstructed, since this design has more

freedom for how the film is held and mounted.

Design #1 had high potential in most of the other categories, especially with the ability to test with

different Radii, and generally scored highly in all of the cateogories. The resulting scores for each design

resulted in a selection of design #1.

Figure 28: Results of Evaluation Matrix tally

With Design #1 selected, there are many questions about how the device will operate. The two main

functions it must serve are to displace linearly to flex the film and to displace in a perpendicular direction

to change the radius. To adjust the height, several options were considered. Most options included using a

motor, which left the decisions to be made if a vacuum rated motor should be used inside of the chamber

or if a mechanical passthrough would provide higher vacuum capabilities. Figure 23 is an initial sketch of

an adjustable height that utilized springs and a string with a spool to adjust the height.

Figure 27: Portion of Evaluation Matrix, highlighting standard adherence

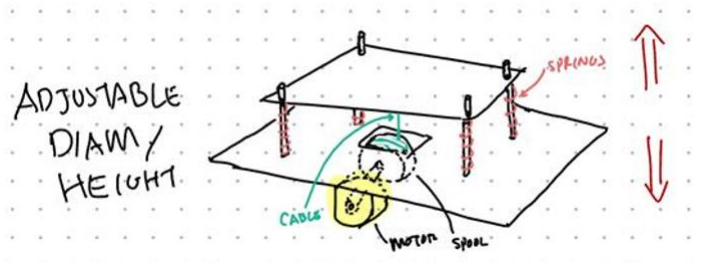
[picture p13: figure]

Figure 29: Sketch showing one method for adjusting the height of a platform using a motor

Another option that was considered was to use a lead screw with gears, which would provide precise

control over the platform height and be stiffer than the other option. If using lead screws, it would the be

necessary to decide between a single screw or multiple. To choose between these options, the main

consideration was complexity and resistance to wear from regolith. The spring method seems very

complex, and it has added issues of the motor requiring a constant holding torque to resist the spring

movement. This could be solved with a one-way torque mechanism, like a worm and worm wheel, but

this is extremely complicated and requires expensive hardware that would be prone to wear. Lead screws

have the advantage of being self-locking and simple to drive. Using four lead screws would be the most

secure option but would likely require many larger gears to split the motor output, which would add mass

to the setup that could increase the cantilevering effect. A single lead screw would be smaller and more compact, but sliders would be required to support the platform on a post which could become stuck or

wear away over with regolith.

Figure 30: Sketch comparing single lead screw configuration to quad configuration

The current plan is to prototype both options and see if either has issues with the mechanism actuating.

By identifying this early in the design process, risk will be eliminated. Another mechanism that required

decision making was on the linear actuation. It could be possible to drive this using a motor or using the

supplied linear actuator. The supplied linear actuator is the preferred design, since it will mount to the

chamber directly and would not require linear slides. Linear slides are a high risk item for regolith to

ingress and eat away, and should be avoided. Vacuum and physical space are the two largest

considerations when making these decisions, since it is important be able to bring the chamber down to

the required vacuum level. This will likely mean some trade-offs have to be made, such as purchasing an

extremely expensive motor that is rated for this level of vacuum, or ditching a mechanism for a linear

actuator as those are easier to buy off the shelf and meet the vacuum requirements.

Figure 25 shows the current up to date CAD, which utilizes groove grabbers to mount to the vacuum

chamber, a lead screw to move the platform, and a linear actuator to move the device. The largest

challenge when constructing this CAD model was with packaging; even small components and plates are

large in proportion to the vacuum mounting geometry.

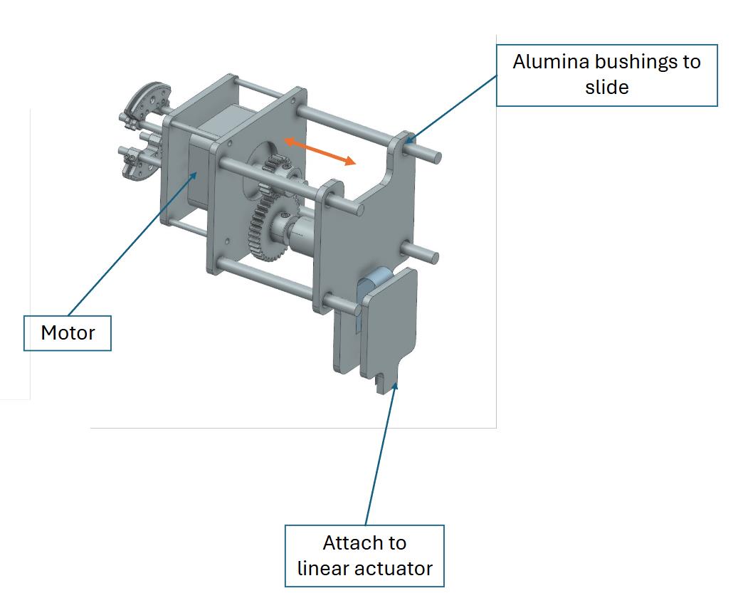
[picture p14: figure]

Figure 31: CAD of proposed design

One open risk is with regolith not being repelled by the film and becoming trapped between the film and

the platform, as shown in Figure 26. This would cause serious damage, as the regolith is extremely

abrasive in nature, and would likely lead to an early failed test. One idea for prevention would be to use a

mesh that would allow the dust to fall off of the film instead of being trapped, which could reduce wear.

Figure 32: diagram showing how regolith can become stuck between film and plate

Another risk for this design is not being able to properly see the film under actuation. When the stroke is

at its full length, the film is visible from the default camera port. However, at the other end of the stroke,

the film is completely blocked by the plate. This could be an issue, if it is desired to view the film under

the full stroke length. However, it may not be necessary to view the film under the full stroke. In this case,

this will not be a concern, but if full view is desired, the camera can be set up to view through the main

viewport instead.

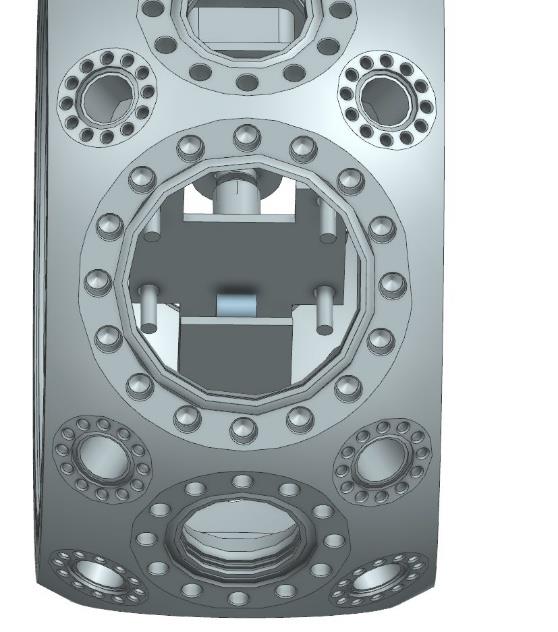
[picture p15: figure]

Figure 33: View of film at bottom of stroke length through standard viewport.

### Industrial Design

Considering the human factors in the design of the final product is important for any capstone group,

including team JD. Even though most of the testing rig will be located inside the high-vacuum chamber

and inaccessible to direct human contact, there are still aspects of the design that could be simplified to

reduce the cognitive load on the user. Namely, the user interface will have to be designed carefully so that

the user understands what they are programming for the controller to perform.

Figure 34: LabView Interface to Interface with the Motor Controller

The number of bending cycles, speed, and stroke length are customizable parameters that the user can

input via a LabView interface. The Current Status tab displays serial output from the controller with

helpful information including the actuator’s current position, target position, speed, and the current loop

cycle its in. The Zero button allows for the user to set the minimum/initial position value of the actuator.

The design can easily integrate with limit switches which would be mounted externally to the vacuum

chamber. This allows for closed loop control, and the motor spins until it hits the end stops of maximum

position and minimum position.

Additionally, the horizontal actuation will be performed manually using the non-powered linear actuator.

This actuator will determine the bending radius of the EDS during testing. After discussing the project

parameters with the key stakeholders, it was important to minimize the number of times that the vacuum chamber had to equalize with atmospheric pressure. Therefore, the bending radius can change without

directly affecting the pressure in the chamber. In terms of industrial design, the actuator is very simple to

operate and ergonomic. To change the bending radius, all the user must do is twist the end of the actuator.

Each full revolution of the dial corresponds to 0.1 mm change in bending radius, allowing for very fine

adjustments of EDS. This minimizes the chances of accidentally over/undershooting the desired radius

and potentially causing damage to the overall system. Furthermore, to visually aid the user when

changing the bending radius, a ruler will be installed inside the vacuum chamber mounted to the EDS

mounting plate that can visually instruct the user as to the current bending radius.

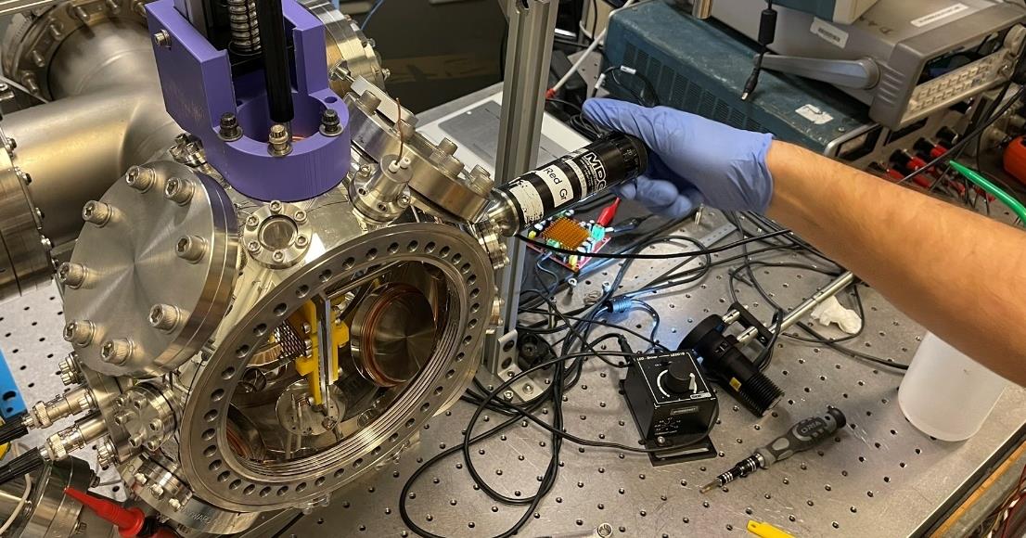
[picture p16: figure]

Figure 35: Demonstration of Variable Bend Radius

Another consideration for the industrial design of the test fixture was how technicians/graduate students

would interface with the clamping fixture. Initial testing revealed that doing all the clamping and

positioning of the EDS to the fixture should be done out of the vacuum chamber. This is due to the size

constraints of the vacuum chamber and the difficulty of fastening bolts in awkward positioning. A further

revision of the mounting plate made this easier to do outside of the chamber, adding to the usability of the

design.

### Engineering Analysis and Experiments

To ensure that the proposed design for the testing rig meets specifications, there are 2 primary forms of

engineering analyses to be performed – fatigue from the cyclic loading the rig enacts on the EDS to

determine part lifetimes and bending/deflection testing from the device’s weight to determine the

necessity of extra mounting. The part most likely to suffer from wear or fatigue in cyclic loading is the

lead screw that adjusts the variable bending radius of the test. Metallic lead screws, which are required in

the high vacuum setting, are typically lubricated to reduce wear from metal-on-metal sliding contact.

However, lubricants cannot be used within the setting of the vacuum chamber, so it is significantly more

susceptible to frictional wear than is standard. Once a motor is officially selected, analysis will be done to

determine the extent to which the lead screw is damaged in this setting.

The other critical consideration is the bending stress and deflection caused by the rig’s weight. The

mounting tools available in the setup provided by GT CLEVER’s lab currently consist of two sets of

Groove Grabbers – devices mounted within the flanges of the vacuum chamber that have threaded

openings and mounts of up to 1/8”. This is a reliable form of mounting, but one set is being used for the

regolith dust dropper leaving one remaining for the rig’s mounting, and with significant price and lead

time considerations, ordering more may not be feasible. Due to this, it is imperative to determine if the

current setup’s deflection falls within the allowable range - 1/10 of the size of the bending radius – to be

deemed unimpactful in data acquisition. This was done via FEA in Siemens NX’s Simcenter with

simplifying assumptions of neglecting contact stresses by joining components together, and preliminary

estimates on the materials used and motor selected. There is an ongoing discussion on whether the EDS

will be powered during testing and if the thin layer of film on top of the substrate insulating the circuit

will be in place, both of which will affect material usage and could alter the results. The constraints

applied are in all 6 translational/rotational DOF at the end of the mounting rods that intersect with the

groove grabber, similar to a cantilever beam. There is an additional constraint about the plane of

symmetry that the device was split in half about (to reduce computational time) to account for the

unmodeled half. The applied load is simply the weight of the device. As shown in Figure. 18, these

parameters yielded a maximum deflection of 0.00103 mm for the testing configuration of 5 mm, only

0.021% of the desired bending radius, well within the acceptable margins.

Figure 36: Deflection FEA of Testing Rig

### Mockup and Prototyping

Team Joint Discovery’s final form of the recommended test setup involves two ultra-high vacuum rated

linear actuators; however, due to the lead time and expenses associated with ordering one, a prototype

was developed to perform testing in a non-vacuum rated setting as a proof of concept. To optimize

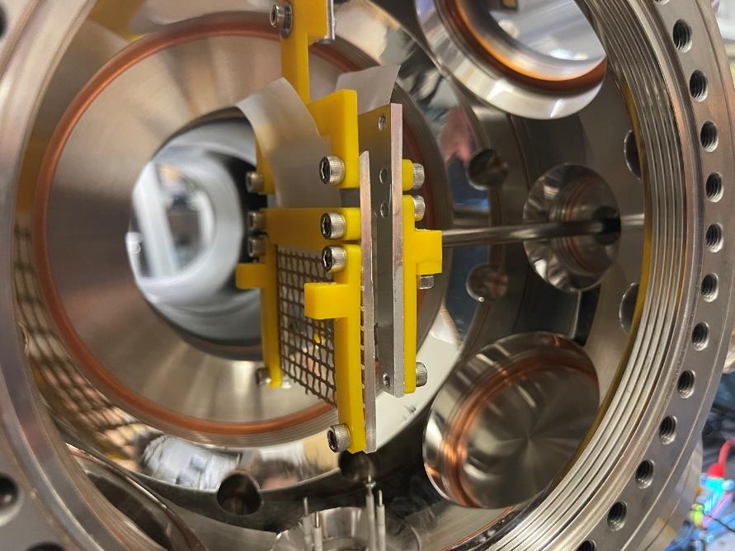
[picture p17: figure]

manufacturing speed, the internal

mounting depicted in Figure 37 were

3D-printed, except for the primary

support plates which required more

stiffness than PLA would provide.

Additionally, a simple strip of PDE

was used as opposed to a sample of

EDS, as power was not running and

current lengths of the EDS would not

showcase the full capabilities of the

adjustable bending radius. Combined,

they produce a robust prototype for

testing, suitable for providing

validity to the recommended stock

purchases and machining efforts

necessary in a vacuum rated version.

External to the vacuum chamber was a high-fidelity prototype linear actuator, depicted in Figure 38

designed to be retrofitted to the lab’s current UHV linear actuator from MDC Precision. Key factors that

were considered in the design of the prototype were replicating the stroke length, internal mounting

interface, flange interface, and ensuring the linear actuating motion was central to the flange it was

Figure 37: Non-Vacuum Rated Testing Prototype Internal Components

Figure 38: High Fidelity Prototype mounted to. An off-the-shelf linear actuator was purchased, selected for its axial load bearing capabilities,

precise stepper motor, and robust mounting capabilities.

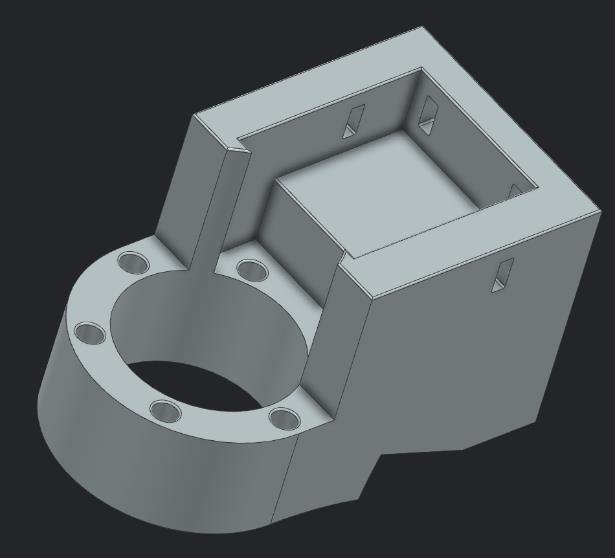
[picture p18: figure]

To replicate the stroke length, minimum and

maximum positions were programmed to the

stepper motor attached to the purchased linear

actuator, although in full testing, limit switches will

be implemented for more reliable results. The

internal mounting system on the UHV actuator

involved a 0.25” diameter rod, faced down ~0.2”

from the end of the rod for 0.75”, and two 6-32

holes. This was recreated with aluminum rod stock

of the same length, lathed down to the appropriate

diameter, faced down and tapped on the mill.

Mirroring the flange interface and aligning the

prototype actuating rod were done with a custom

3D-print shown in Figure 37. Its features include a

face with the same necessary mounting dimensions as the DN16CF on the UHV linear actuator, but with a

smaller inner diameter to avoid infringing upon the delicate knife edge on the vacuum chamber’s flange.

To ensure a known alignment of the actuator, the print also included a slot for the purchased linear

actuator with an interference fit, highlighted in Figure 39, and slots to further secure it with threaded

fasteners. Then to make the rod align in the middle of the flange, the aluminum stock connecting the

actuating rod to the guided mount on the actuator was machined down to the appropriate height.

Maintaining stability was also crucial for the demonstration, so the part is curved to maintain more

surface contact with the vacuum chamber and has extrusions to allow it to sit on existing flanges, depicted

in Figure 40. The result was a robust prototype linear actuator with the necessary features and testing

capabilities to recommend a known UHV counterpart.

Figure 39: 3D-Printed Flange Interface and Linear Actuator Mount

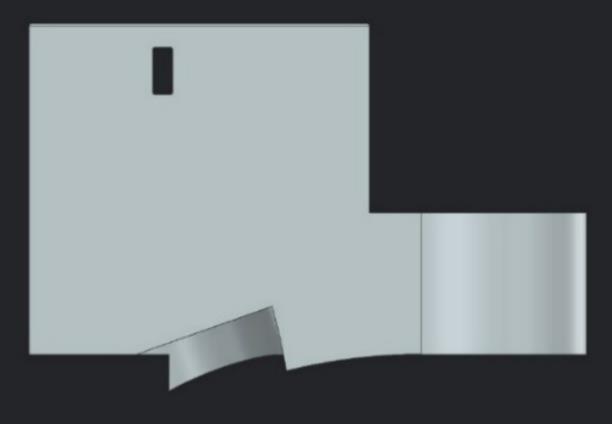
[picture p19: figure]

Figure 41: Side View of 3D-Printed Flange Interface and Linear Actuator Mount

Figure 40: Side View of 3D-Printed Flange Interface and Linear Actuator Mount

### Final Design

The final design for the system consists of two

subassemblies, each actuated with a linear passthrough

into the chamber. By taking advantage of off-the-shelf,

vacuum rated passthroughs, the team was able to

simplify the design and improve reliability. Each linear passthrough is rated to a vacuum of 10⁻⁸
torr, which is

sufficient for the needs of the client. The vertical

passthrough is motorized to allow for automated

sweeping and cyclic repetition of the film. This will be

seamlessly integrated with the LabVIEW interface for

simple control.

The horizontal actuation is used to adjust the film

bending radius, which is a requirement to accurately

test the chosen standard. This actuation is done by

hand using the horizontal linear passthrough, which

can be accurately determined by first zeroing the

plates by touching them together and then backing off

to the desired bend radius. It should be noted that the

horizontal passthrough stroke is directly tied to the

diameter of the film, ex. a 10mm backout of the

actuator results in a +5mm bend radius. The smallest

bend radius, when the two plates are touching, is

2mm, as mandated by the minimum thickness of the

film plates during manufacturing.

Figure 43: Variable adjustment of bending radius

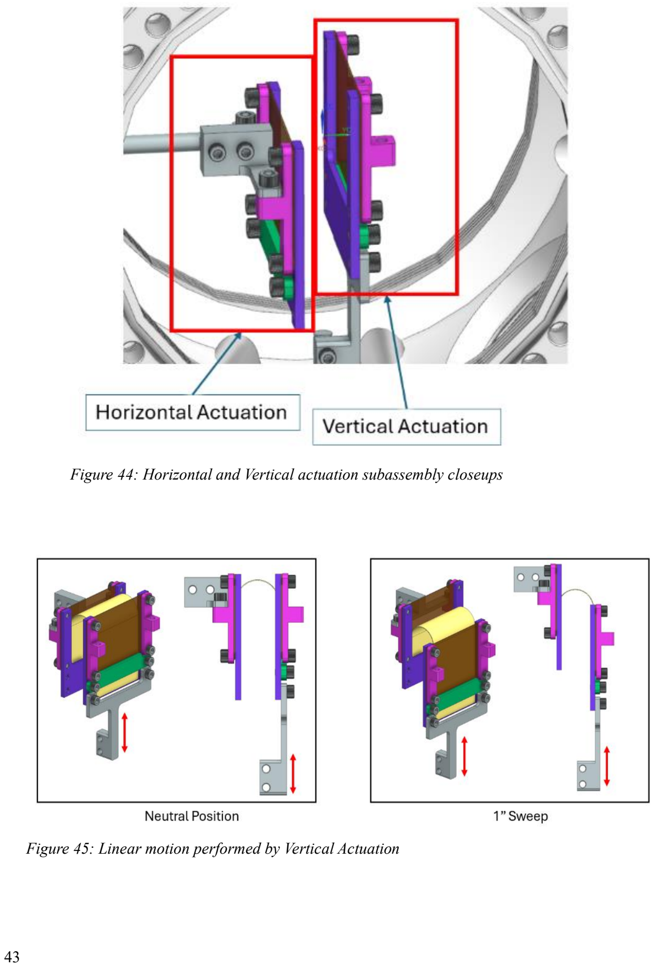
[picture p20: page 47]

Figure 45: Linear motion performed by Vertical Actuation

Figure 44: Horizontal and Vertical actuation subassembly closeups

The vertical actuation is the main sweeping motion, which repeats for any number of cycles to meet the

client’s requirements. The vertical actuation is motorized, and can perform any number of cycles. It is

important for the user to properly setup up the actuation restriction zones, so the assembly does not over-

extend and clash the fixture into the chamber.

The system was designed to fit within the chamber and not occlude the Dust Falling System (DFS), but has

a larger stroke length without the DFS installed. The final capabilities are listed below. The only original

requirement that was unmet by the system is for the stroke length, which falls slightly below 2”. This is due

to a limitation of the linear actuator and packaging of the device under the DFS, but it will still be proficient

for the client’s needs.

Table 4: Customer Required Dimensions

Dimension | Capability | Requirement
Stroke Length | 45mm (1.8”) | 2”
Min Radius | 2mm | 2mm
Max Radius | 13.5mm | 10mm
Max Film Width | 53mm | 50mm

Figure 46: Vertical and Horizontal adjustment ability

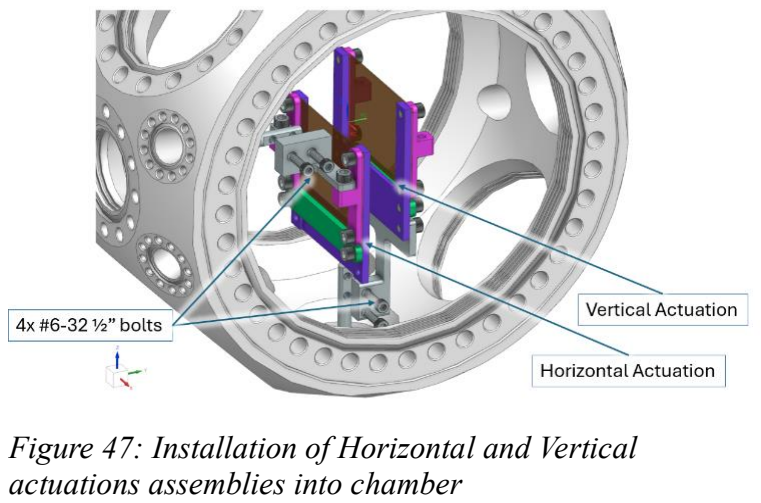
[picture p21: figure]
actuations assemblies into chamber

After the initial vacuum chamber test, the team found it

was difficult to properly assemble the device within the

chamber due to limited access. Furthermore, the client

brought to attention the need to assemble the film into the

clamping device before being installed in the chamber, as

this will reduce the risk of damage to the electrical leads.

The horizontal and vertical mounts have been designed to

allow easy mounting to the linear actuators after the film

has been attached. The bolts are conveniently oriented to

allow tightening from opening in the main chamber.

Assembly of each sub-assembly is simple, requiring only

a few screws and the machined pieces. The mesh is held

tightly in place by the mesh clamps, which act to clamp

the fiberglass fabric down to the film plate. This method

allows easy changing of mesh materials if desired, and

provides a rigid mechanical connection that avoids

adhesives which may lead to unfavorable results in ultra-

high vacuum conditions. The purpose of the fiberglass

fabric is to prevent buildup of lunar regolith during

falling. The mesh pictured in the CAD is solid, but the

real mesh is showed below.

It was important for the client to have a strong mechanical

connection holding the film in place. Previous methods

included using a double sided tape, but to ensure a strong

consistent connection through multiple cycles, the team

implemented a clamping method.

All of the parts are either bought off the shelf (COTS) from a

supplier or need to be machined out of aluminum. Below is an

example of a drawing that can be directly given to a machine

shop to produce the required part. The full set of drawings

and links to COTS are found in the final fabrication package,

including the full BOM.

using Mesh Clamps

Figure 47: Installation of Horizontal and Vertical

Figure 49: Mesh installed on prototype assembly

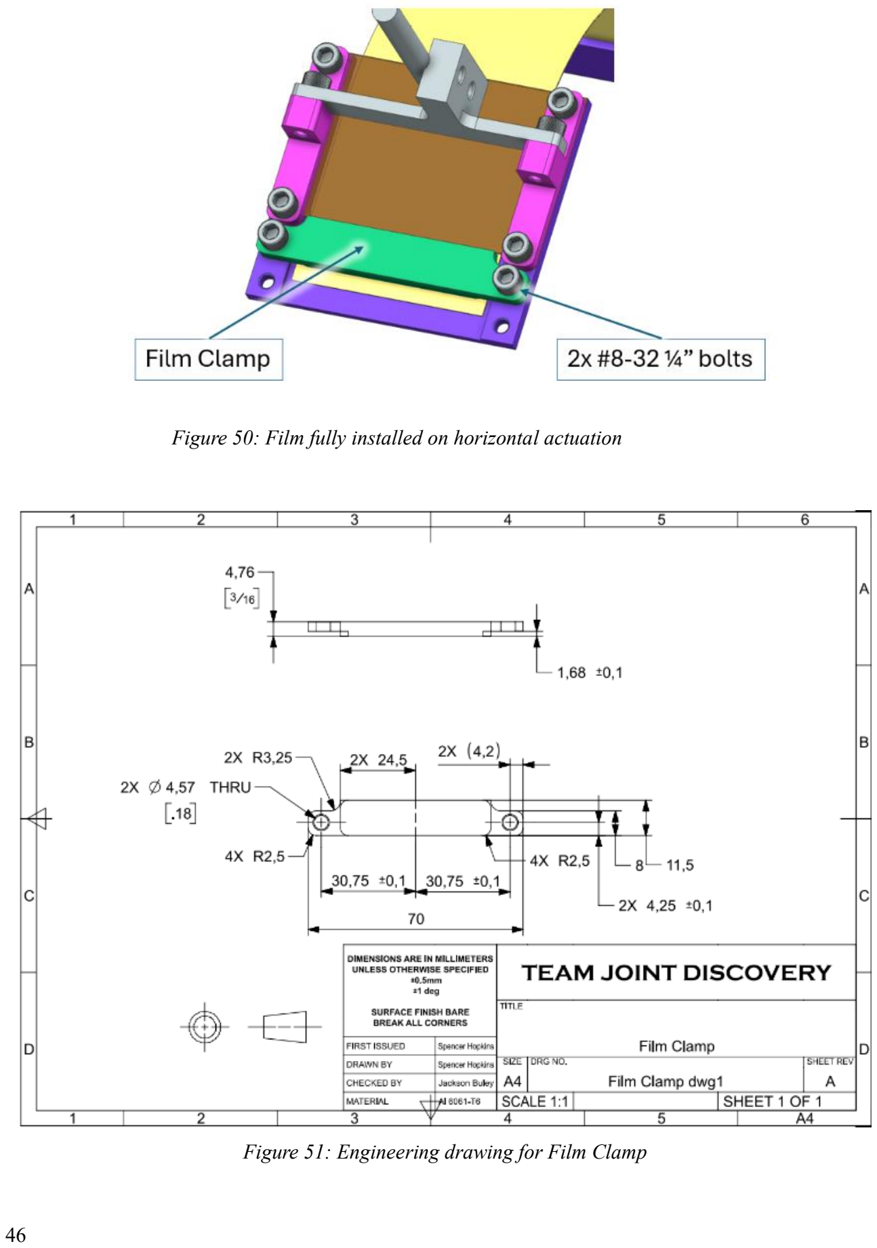
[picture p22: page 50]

Figure 50: Film fully installed on horizontal actuation

Figure 51: Engineering drawing for Film Clamp

### Manufacturing

Design for manufacturing was a critical element of the project throughout all stages of development. Even

though the final product is not intended to be mass produced, manufacturing is still a critical element of

the overall design considerations. Namely, because of the vacuum environment, the final product had to

be machined from metal. This is because metals do not experience outgassing effects that could damage

the internal equipment inside the vacuum chamber.

For prototyping, this was not a major concern as the initial testing was conducted in ambient conditions.

As such, the initial design could be 3D printed from standard PLA to reduce cost and time from

manufacturing with metal. While the prototyping provided a physical way to validate the geometry of the

components together, the resolution of the printer was too low to allow for any threaded connections.

Purchasing a vacuum-rated linear actuator was too expensive for the prototype budget. Because of this,

team JD designed a non-vacuum rated linear actuator that could be put in place. The non-vacuum rated

actuator needed to have the same dimensions as the vacuum rated counterpart to validate the overall

system could function. In the end, the design for the prototype actuator consisted of 4 parts: off the shelf

motorized actuator, metal connecting block, vacuum chamber mounting flange, and actuating arm.

The tolerances on the manufacturing of the prototype linear actuator were very tight; within ±0.05mm for

spacing between holes (tightest parameter) and ±0.5mm for overall size dimensions. Both the metal

connection block and actuating rod were machined out of aluminum stock using the Montgomery

Machining Hall. While it is not necessary for the final product, these machined parts were critical for the

prototyping to ensure the system could function properly. At the end of the actuating rod were two holes

that needed to be machined to closely match the connection points of the vacuum rated actuator. Special

care and attention were taken to ensure the tolerances fell within the allotted ±0.005” and the overall

system could be connected to it.

Furthermore, while parts of the mounting plate were 3D printed from PLA material, the final product will

have to be machined from aluminum stock. As such, when designing the final product, care was taken

towards designing the overall plate to be flat and easily machined. It used standard threaded connections

that are repeated throughout the design of the mounting plate so no more than one tap must be used.

Figure 52: Engineering Drawing for Film Plate

When designing the final film plate, team JD was able to construct their own threaded connections and

through holes. As such, the tolerancing on the final product is ±0.5mm. However, the thickness of the part

must be machined to within ±0.1mm. This is because the height of the film plate is crucial to know the

bend radius of EDS accurately.

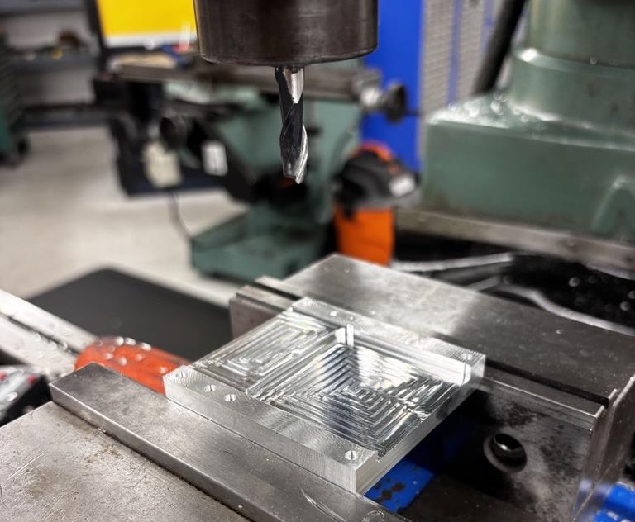
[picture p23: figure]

Figure 53: Machining the Film Plate

Overall, the part was designed to be machined from standard aluminum stock (Al 6061). The material is

relatively low cost and easily obtainable for manufacturing. It is one of the most common aluminum

alloys used in general purpose machining, such as this. Al 6061 also has the added benefit of use in an

ultra-high vacuum environment. Because of its abundance and ease in machining, this alloy was selected

as the material for the final product.

### Societal, Environmental, and Sustainability Considerations

This section will implement the Social Impact Assessment as outlined in the ME Capstone website

(Social Impact Assessment (SIA) for Capstone Design, 2020).

1. Goal and Scope

This section depicts the goal and scope of the Social Impact Assessment.

Table 5: Goal and Scope Section Summary

Objective of Assessment | Design Function | Functional Unit | Lifecycle Stages Considered | Associated Activities
Assess the societal impacts of a flexible EDS for lunar applications | Repel lunar regolith from flexible/curved surfaces. | A strip of flexible EDS | Production | The creation and production of the EDS

Test and validation of

EDS

Local job creation

Use | The effectiveness of the EDS on the moon
End-of-life | Not creating lunar waste
2. Societal Impact Categories and Indicators

This section discusses the social impact categories and impact indicators.

Table 6: Inventory Analysis Section Summary

Lifecycle Stage | Stakeholder Group | Social Impact Category | Impact Indicators
Production | Worker | Health and Safety | Appropriate protective gear required in all applicable

situations

Occupational accident

rate

Worker | Health and Safety

Presence of a formal

policy concerning

health and safety

Adequate general

occupational safety

measures

are taken

Local Community | Local Prosperity | Creation of high-tech jobs
Use | Consumer | Feedback Mechanism | Investment in local R&D infrastructure

Number of consumer

complaints per square

foot of EDS installed

End-of-life | Society (Humanity) | Transgenerational Responsibility

Presence of a

decommissioning

plan/adherence to

"leave no trace"

principles on the

Moon

3. Reflection on Societal Impacts

The evaluation and eventual end use of a flexible EDS will have a net positive impact on humanity’s

wellbeing with some potential negative impacts that require mitigation.

The primary impact is that this will provide safeguarding of both humans who are interacting with objects

that are protected using a flexible EDS as well as by ensuring mission success of components that would

suffer from the presence of lunar dust. Further, this project would further stimulate high-tech job creation

and research and development infrastructure as generated during the production and test life cycles of the project. By attempting to produce the least amount of additional lunar waste (by the nature of flexible

EDS being a solid-state device), this project emphasizes the principle of transgenerational responsibility

by preserving the lunar environment.

There are potentially negative impacts from this project, including worker safety. During the production

and testing stages, the workers will be handling specialized materials/chemicals as well as being

potentially exposed to high voltage. If the flexible EDS ends failing before their expected life cycle, it

could potentially contribute to increased lunar waste as well as impacting the lifespans of the

objects/devices it is intended to protect.

This section focused on the production, use, and end-of-life lifecycle stages as they represent the most

socially consequential phases of this technology. The stakeholder groups were selected based on those

directly affected by the technology, such as the workers developing and producing the technology. The

stakeholders further include the consumers who are the direct beneficiaries of their functionality, and then

the larger scale societal impacts are considered as well. Indicators and categories were selected to map

measurable outcomes and goals for the selected stakeholders.

### Risk Assessment, Safety and Liability

Potential risks stem from the recommended vacuum rated testing procedures. Artificial regolith poses a

significant hazard to human health if released breathed in or ingested. GT CLEVER must follow the

safety procedures associated with the loading and use of the dust dropping mechanism. Additionally, if

testing is run when the EDS is powered, there must be measures taken to avoid either contact between the

conductive grid or effectively ground the current. This affected the design of the internal mounting

components in recommending the use of alumina for a less conductive material, and in providing another

reason to using and actively powered EDS in testing.

Figure 54: Testing with the Lunar Simulant Requires Gloves and Fume Hood to Prevent Exposure

Team JD also took care of prototyping to avoid damaging the vacuum chamber due to its significant cost

and necessity in GT CLEVER’s research. Certain components of the UHV linear actuator’s flange

interface were not replicated in the 3D printed replica to avoid unnecessary contact with the knife edge on

the chamber’s corresponding flange. If the chamber was damaged, it would negatively impact the overall

vacuum rating and cost the lab potentially thousands of dollars to repair. Additionally, the internal

mounting system applied crucial design for assembly features in applying appropriate spacing between

the parts and the external walls of the chamber to prevent contact when assembling.

During prototyping, it was found that manually setting the limit switches proved to be difficult. This

resulted in the need for a “kill switch”, a simple on/off switch that could turn off the mechanism in an

instant. This was necessary so that the actuator did not extend far enough to touch the vacuum chamber

walls and/or damage the chamber walls. While critical for the prototyping phase, the use of limit switches

in the final product will eliminate the need for this fail-safe. Limit switches provide a physical barrier for

the actuator to prevent it from extending too far inside of the chamber.

### Patent Claims and Commercialization

Team JD has no patent claims over our design. The team believes that by keeping the design open source,

it will enable researchers to iterate over our design and make improvements to enable EDS studies while

the system is powered. This report, and all associated documents will be hosted on a public GitHub

repository available here: https://github.com/s-callaway/Team-Joint-Discovery-Bending-EDS

In addition, the team has no plans or prospects for commercialization. The team hopes to help researchers

progress in the field of electrodynamic shielding. The only opportunity the team is considering is

recognition in any journal that future work may be published involving the bending prototype the team

developed.

### Team Member Contributions

Jackson Buley (Mechanical Engineering): Jackson Buley worked closely with Drew Peljovich to distill

House of Quality, FMEA, and specifications documents from our sponsor meetings. He also performed

the FEA and engineering analysis. Jackson also contributed to the design of the linear actuator mount that

imparted bending on the EDS.

Drew Peljovich (Mechanical Engineering): Drew led the writing and presentation work. He distributed

the report work and worked closely with Jackson Buley to complete the House of Quality, FMEA, and

Spec sheet. Drew created the LabVIEW interface for our clients (the graduate students) to autonomously

control the stepper motor. In addition, he and Jackson worked together to machine or final design parts.

Spencer Hopkins (Mechanical Engineering): Spencer developed the in-depth drawings and developed the

CAD for the final design. Spencer developed and printed our final prototypes as well. Spencer conducted

much of the original work into standards research and led the mechanical design to meet customer

requirements.

Vikas Muralidharan (Material Science and Engineering): Vikas acted as the project manager and gave

insight into the uses and materials of the EDS device. He developed the Gantt chart as well as helped

Jackson Buley set up meetings with sponsors. He also developed the poster for the capstone expo.

Sasha Callaway (Computer Engineering): Sasha Callaway contributed the bulk of the market research for

EDS and helped iterate one potential design choice given his background with PCB’s. He further did

research into the flexible PCB related standards and implemented the social impact assessment. He wrote

the budget appendix, existing products and prior art, as well as industrial design.

### Summary and Future Work

In summary, Team JD has successfully designed a compact, vacuum-compatible bending rig for flexible

EDS films. The primary challenge of this project was to design a repeatable bending mechanism that

could operate under ultra‑high vacuum while accommodating limited electrical passthroughs and

mechanical interfaces. To address this, the team developed a rig that leverages the existing linear bellows

drive to cyclically bend the EDS film, ensuring both repeatability and cost efficiency. The design

successfully balances the chamber’s strict constraints with functional requirements, allowing for

simultaneous dust deposition and electrical activation of the EDS. This rig serves as a critical

proof‑of‑concept platform for validating flexible EDS technology, advancing its readiness for

commercialization and deployment in lunar missions. Unlike prior art, it uniquely addresses cyclic

bending of flexible thin‑films in vacuum, filling an important gap in current testing systems.

The next steps for this project involve fabricating the rig and conducting experimental validation under

vacuum, including cyclic bending with dust deposition and EDS activation. Long‑term durability studies,

such as testing beyond 1,000 cycles, will be needed to assess fatigue resistance and cleaning efficiency.

Incorporating cameras and sensors will enable real‑time monitoring of dust removal and bending

performance, while future design refinements may explore modularity to allow variable bending radii,

torsional loading, and integration with larger chamber setups.

To prepare the system for the vacuum environment, all the materials that exist directly inside the vacuum

chamber must be machined from an aluminum alloy to withstand the extreme low-pressure conditions

using the fabrication package. Furthermore, purchasing one motorized linear actuator is necessary to

perform cyclic bending in the vacuum environment. Standoffs need to be incorporated into the design to

raise the vacuum chamber and mount the vertical linear actuator underneath to allow for dust deposition

in the process. Exact dimensions cannot be determined until a quote is requested for the part, as the

manufacturer does not provide that information readily. The final change would be the addition of limit

switches to provide more robust control near the minimum and maximum displacement. These switches

have bolt holes for securing to the linear actuator and will be pressed by the linear actuator’s position

indicator. The code for implementing these switches already exists in the Arduino code, but the physical

implementation is needed.

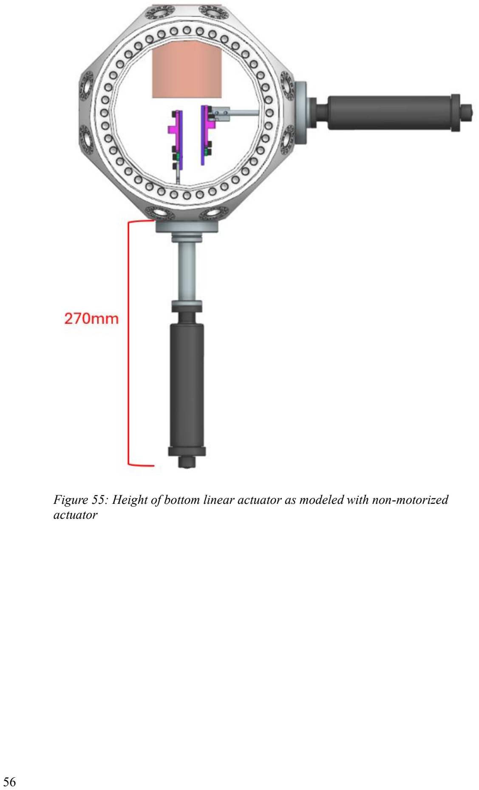
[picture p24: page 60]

Figure 55: Height of bottom linear actuator as modeled with non-motorized actuator

### Bibliography

Astrobotic Payload Management. (2021, August). ASTROBOTIC LUNAR LANDERS. Retrieved from

Astrobotic Technology: https://www.astrobotic.com/wp-

content/uploads/2022/01/PUGLanders_011222.pdf

Freche, J. C. (1965). The effect of vacuum on the fatigue and stress-rupture properties of s-816 and

inconel 550 at 1500 deg f. Cleveland: NASA. Retrieved from

https://ntrs.nasa.gov/citations/19650017054

Gaier, J. R. (2007). The Effects of Lunar Dust on EVA Systems During the Apollo Missions. Technical

Memorandum, NASA, Washington, DC. Retrieved from

https://ntrs.nasa.gov/api/citations/20070021819/downloads/20070021819.pdf

K, M. K. (2024, October 22). United States of America Patent No. US-12121910-B2.

Li, W. (2024). Understanding People, Products and Context: Industrial Design Lite for Engineering.

Slideshow, Georgia Institute of Technology, George W. Woodruff School of Mechanical

Engineering, Atlanta. Retrieved from https://bpb-us-

e1.wpmucdn.com/sites.gatech.edu/dist/2/334/files/2024/01/IDLite_UseContext_Sp24-

e21f5c3685b8782a.pdf

Mazumder, M. K. (2013, October 10). United States of America Patent No. US-9433336-B2.

(2020). Social Impact Assessment (SIA) for Capstone Design. Outline, Georgia Institute of Technology,

George W. Woodruff School of Mechanical Engineering, Atlanta. Retrieved from https://bpb-us-

e1.wpmucdn.com/sites.gatech.edu/dist/2/334/files/2020/01/SIA_Outline_final.pdf

Tatom, F. B. (1967). LUNAR DUST DEGRADATION EFFECTS AND REMOVAL/PREVENTION

CONCEPTS FINAL REPORT. Technical Report No. 321, NASA, Propulsion and Vehicle

Engineering Laboratory, Huntsville. Retrieved from NASA:

https://ntrs.nasa.gov/api/citations/19680009551/downloads/19680009551.pdf

TC 119 - Printed Electronics. (2018, September 27). Printed electronics - Part 202-5: Materials -

Conductive ink - Mechanical bending test of a printed conductive layer on an insulating

substrate. Retrieved from standards.iteh.ai:

https://standards.iteh.ai/catalog/standards/sist/08e89f8d-dc0a-47ba-9875-61186aa2ecba/iec-

62899-202-5-2018

Technical Committees of IPC. (2022, May). IPC-TM-650 Test Methods Manual. (F). Bannockburn,

Illinois. Retrieved from electronics.org.

A

### Appendix

Figure 56: Full Morphological Chart

B

Figure 57: ESP32 Based Motor Controller Board Pinout (full file in GitHub)

Figure 58: ESP32 Based Motor Controller Board

C

### Budget Appendix

Category | Item Description | Part Number / Link | Quantity | Unit Cost (USD) | Subtotal (USD)
Linear Motion | Prototype Linear Actuator | B085SXDS2B (https://www.amazon.com/dp/B085SXDS2B?th=1) | 1 | 73.80 | 73.80
Structural Materials | Multipurpose 6061 Aluminum Bar | 8975K237 | 1 | 17.64 | 17.64
Structural Materials | Linear Motion Shaft | 1031K12 | 1 | 16.61 | 16.61
EDS Mounting Prototypes | PTFE-Coated Fiberglass | 87865K44 (https://www.mcmaster.com/87865K44/) | 1 (1ft) | 34.33 | 34.33
EDS Mounting Prototypes | HDPE Mesh Fabric | 88275K43-88275K431 (https://nam12.safelinks.protection.outlook.com/?reserved=0) | 1 (1ft) | 9.63 | 9.63
EDS Mounting Prototypes | HDPE Mesh Fabric | 88275K39-88275K391 (https://nam12.safelinks.protection.outlook.com/?reserved=0) | 1 (1ft) | 6.01 | 6.01
EDS Mounting Prototypes | Stainless Steel | 85385T28 (https://nam12.safelinks.protection.outlook.com/?url=https%3A%2F%2Fwww.mcmaster.com%2F85385T28&reserved=0) | 1 (1ft) | 20.62 | 20.62
EDS Mounting Prototypes | Stainless Steel | 85385T24-85385T813 (https://nam12.safelinks.protection.outlook.com/?reserved=0) | 1 (1ft) | 16.97 | 16.97
Electronics and Wiring | ESP32 Microcontroller | ESP32-C6 (https://nam12.safelinks.protection.outlook.com/?reserved=0) | 1 | 18.99 | 18.99
Electronics and Wiring | Motor Driver | A4988 (https://www.amazon.com/Stepper-Compatible-Stepstick-Printer-Robotics/dp/B09FQ3G5XQ?linkId=3d405814921cfd3b11a5c53327086e43) | 1 | 13.99 | 13.99
TOTAL COST | | | | | $228.59

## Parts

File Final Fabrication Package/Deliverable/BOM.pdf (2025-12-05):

Item | Description | Link | Cost | Qty
#8-32 1/4" Stainless Steel Socket Head Screw | Plate Fastening Screws | https://www.mcmaster.com/92196A190 $ | | 1 7.21

#6-32 1/2" Stainless Steel

Socket Head Screw | Linear Actuator Screws | https://www.mcmaster.com/92196A148 $ | 1 7.62
MDC Precision Linear Motion
Feedthrough | Radius Adjustment Linear Actuator | https://www.mdcprecision.com/parts/linear-motion-feedthrough-133-flange-2-travel $ | 1 996.00 | *Already in lab
MDC Precision Linear Motion Feedthrough | Linear Sweeping Actuator | https://www.mdcprecision.com/parts/linear-motion-feedthrough-133-flange-2-travel ?? | 1 | *Need to select motorized option
2.75" Flange Adapter (Reduce to 1.33" CF) | Linear actuator flange adapter | https://www.kimballphysics.com/product/mcf275-flgadptr-c1a1/ $ | 2 288.00 | *At least one already in lab
| | PTFE-Coated Fiberglass Fabric Sheet, Mesh, 40" Wide | McMaster-Carr $ 34.33 | 1
Film Plate | TOBE MACHINED | Drawing in Fabrication Package | 2
Film Clamp | TOBE MACHINED | Drawing in Fabrication Package | 2
Mesh Clamp | TOBE MACHINED | Drawing in Fabrication Package | 4
Vertical Connector | TOBE MACHINED | Drawing in Fabrication Package | 1
Horizontal Connector | TOBE MACHINED | Drawing in Fabrication Package | 1

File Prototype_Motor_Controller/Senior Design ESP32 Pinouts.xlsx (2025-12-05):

ESP32-C6
J1 USB |  |  |  |  |  |  | J3 UART
Connection | Breadboard Connection | Breadboard | Type (https://docs.espressif.com/projects/esp-dev-kits/en/latest/esp32c6/esp32-c6-devkitc-1/user_guide_v1.1.html) | Function | Name | No. | No. | Name | Function | Type | Breadboard | Breadboard Connection | Connection
NC | NC | A_B_21 | P | 3.3V Power | 5V | 1 | 1 | 5V | 5 V power supply | P | A_T_21 | NC | NC
Left breadboard Ground | A_B_- | A_B_22 | G | Ground | GND | 2 | 2 | 13 | GPIO13, USB_D+ | I/O/T | A_T_22 | B_T_9 | DIRECTION_A
NC | NC | A_B_23 | I/O/T | GPIO9 3 (https://docs.espressif.com/projects/esp-dev-kits/en/latest/esp32c6/esp32-c6-devkitc-1/user_guide_v1.1.html) | 9 | 3 | 3 | 12 | GPIO12, USB_D- | I/O/T | A_T_23 | B_T_10 | STEP_A
Limit Switch A | A_T_9 | A_B_24 | I/O/T | GPIO18, SDIO_CMD, FSPICS2 | 18 | 4 | 4 | 11 | GPIO11 | I/O/T | A_T_24 | B_T_12 | nRESET_A
Limit Switch B | A_T_12 | A_B_25 | I/O/T | GPIO19, SDIO_CLK, FSPICS3 | 19 | 5 | 5 | 10 | GPIO10 | I/O/T | A_T_25 | B_T_16 | nENABLE_A
NC | NC | A_B_26 | I/O/T | GPIO20, SDIO_DATA0, FSPICS4 | 20 | 6 | 6 | 8 | GPIO8 2 3 | I/O/T | A_T_26 | NC
NC | NC | A_B_27 | I/O/T | GPIO21, SDIO_DATA1, FSPICS5 | 21 | 7 | 7 | 1 | GPIO1, XTAL_32K_N, LP_GPIO1, LP_UART_DSRN, ADC1_CH1 | I/O/T | A_T_27 | B_T_19 | DIRECTION_B
NC | NC | A_B_28 | I/O/T | GPIO22, SDIO_DATA2 | 22 | 8 | 8 | 0 | GPIO0, XTAL_32K_P, LP_GPIO0, LP_UART_DTRN, ADC1_CH0 | I/O/T | A_T_28 | B_T_20 | STEP_B
NC | NC | A_B_29 | I/O/T | GPIO23, SDIO_DATA3 | 23 | 9 | 9 | 7 | MTDO, GPIO7, LP_GPIO7, LP_I2C_SCL, FSPID | I/O/T | A_T_29 | B_T_22 | nRESET_B
NC | NC | A_B_30 | I/O/T | GPIO15 3 (https://docs.espressif.com/projects/esp-dev-kits/en/latest/esp32c6/esp32-c6-devkitc-1/user_guide_v1.1.html) | 15 | 10 | 10 | 6 | MTCK, GPIO6, LP_GPIO6, LP_I2C_SDA, ADC1_CH6, FSPICLK | I/O/T | A_T_30 | B_T_26 | nENABLE_B
EMPTY |  |  | I/O/T | U0RXD, GPIO17, FSPICS1 | RX | 11 | 11 | 5 | MTDI 3, GPIO5, LP_GPIO5, LP_UART_TXD, ADC1_CH5, FSPIWP (https://docs.espressif.com/projects/esp-dev-kits/en/latest/esp32c6/esp32-c6-devkitc-1/user_guide_v1.1.html) | I/O/T | EMPTY
NC | NC | B_B_1 | I/O/T | U0TXD, GPIO16, FSPICS0 | TX | 12 | 12 | 4 | MTMS 3, GPIO4, LP_GPIO4, LP_UART_RXD, ADC1_CH4, FSPIHD (https://docs.espressif.com/projects/esp-dev-kits/en/latest/esp32c6/esp32-c6-devkitc-1/user_guide_v1.1.html) | I/O/T | B_T_1 | NC | NC
NC | NC | B_B_2 | I/O/T | GPIO3, LP_GPIO3, LP_UART_CTSN, ADC1_CH3 | 3 | 13 | 13 | RST | High: enables the chip; Low: disables the chip. | I | B_T_2 | NC | NC
NC | NC | B_B_3 | I/O/T | GPIO2, LP_GPIO2, LP_UART_RTSN, ADC1_CH2, FSPIQ | 2 | 14 | 14 | 3V3 | 3.3 V power supply | P | B_T_3 | B_T_+ | Right Breadboard Plus
Right Breadboard Ground | B_B_- | B_B_4 | G | Ground | GND | 15 | 15 | GND | Ground | GND | B_T_4 | B_T_- | Right Breadboard Ground
A4988 Driver A (TOPSIDE) |  |  |  |  |  |  |  |  |  |  |  |  |  | A4988 Driver (from photo)
J1 |  |  |  |  |  |  | J2 |  |  |  |  |  |  | J1 |  | J2
Connection | Breadboard Connection | Breadboard | Type |  | Name | No. | No. | Name |  | Type | Breadboard | Breadboard Connection | Connection | Name | No. | No. | Name
G_ESP | B_B_- | B_B_9 | G |  | GROUND | 1 | 1 | DIRECTION_A |  | I | B_T_9 | B_T_1 | 12_4_ESP | DIRECTION | 1 | 1 | GROUND
3V3_ESP | B_T_+ | B_B_10 | P |  | VDD | 2 | 2 | STEP_A |  | I | B_T_10 | A_T_23 | 7_21_ESP | STEP | 2 | 2 | VDD
1_B_M_A | B_B_11 | B_B_11 | O |  | 1B | 3 | 3 | nSLEEP_A |  | I | B_T_11 | B_T_10 | STEP_A | nSLEEP | 3 | 3 | 1B
1_A_M_A | B_B_12 | B_B_12 | O |  | 1A | 4 | 4 | nRESET_A |  | I | B_T_12 | A_T_24 | 4_11_ESP | nRESET | 4 | 4 | 1A
2_A_M_A | B_B_13 | B_B_13 | O |  | 2A | 4 | 4 | MS3_A |  | I | B_T_13 | NC | NC | MS3 | 4 | 4 | 2A
2_B_M_A | B_B_14 | B_B_14 | O |  | 2B | 5 | 5 | MS2_A |  | I | B_T_14 | NC | NC | MS2 | 5 | 5 | 2B
G_M | B_T_- | B_B_15 | G |  | GROUND | 6 | 6 | MS1_A |  | I | B_T_15 | NC | NC | MS1 | 6 | 6 | GROUND
VMOT_M |  | B_B_16 | P |  | VMOT | 7 | 7 | nENABLE_A |  | I | B_T_16 | A_T_25 | 5_10_ESP | nENABLE | 7 | 7 | VMOT
A4988 Driver B (TOPSIDE) |  |  |  |  |  |  |  |  |  |  |  |  |  | A4988 Driver (TOPSIDE)
J1 |  |  |  |  |  |  | J2 |  |  |  |  |  |  | J1 |  | J2
Connection | Breadboard Connection | Breadboard | Type |  | Name | No. | No. | Name |  | Type | Breadboard | Breadboard Connection | Connection | Name | No. | No. | Name
G_ESP | B_B_- | B_B_19 | G |  | GROUND | 1 | 1 | DIRECTION_B |  | I | B_T_19 | A_T_27 | 7_1_ESP | GROUND | 1 | 1 | DIRECTION
3V3_ESP | B_T_+ | B_B_20 | P |  | VDD | 2 | 2 | STEP_B |  | I | B_T_20 | A_T_28 | 8_0_ESP | VDD | 2 | 2 | STEP
1_B_M_B | B_B_21 | B_B_21 | O |  | 1B | 3 | 3 | nSLEEP_B |  | I | B_T_21 | B_T_20 | STEP_B | 1B | 3 | 3 | nSLEEP
1_A_M_B | B_B_22 | B_B_22 | O |  | 1A | 4 | 4 | nRESET_B |  | I | B_T_22 | A_T_29 | 9_7_ESP | 1A | 4 | 4 | nRESET
2_A_M_ | B_B_23 | B_B_23 | O |  | 2A | 4 | 4 | MS3_B |  | I | B_T_23 | NC | NC | 2A | 4 | 4 | MS3
2_B_M_B | B_B_24 | B_B_24 | O |  | 2B | 5 | 5 | MS2_B |  | I | B_T_24 | NC | NC | 2B | 5 | 5 | MS2
G_M | B_T_- | B_B_25 | G |  | GROUND | 6 | 6 | MS1_B |  | I | B_T_25 | NC | NC | GROUND | 6 | 6 | MS1
VMOT_M |  | B_B_26 | P |  | VMOT | 7 | 7 | nENABLE_B |  | I | B_T_26 | A_T_30 | 10_6_ESP | VMOT | 7 | 7 | nENABLE

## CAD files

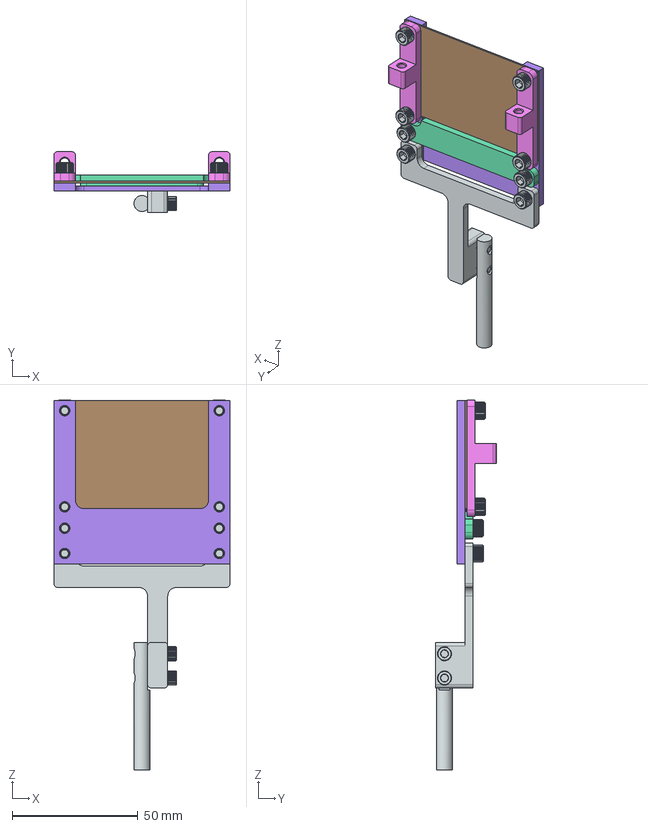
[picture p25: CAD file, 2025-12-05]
Final Fabrication Package/CAD/ASSEM_Vertical Actuation Assembly.stp
70.0 x 24.1 x 147.2 mm
Vertical Mount
Mesh Clamp x 2
Film Plate
Film Clamp
Vertical Actuator Tip
6_32 UNC 1_2in 18_8 Screw 92196A190 x 8
8_32 UNC 1_4in 18_8 Screw 92196A148 x 2

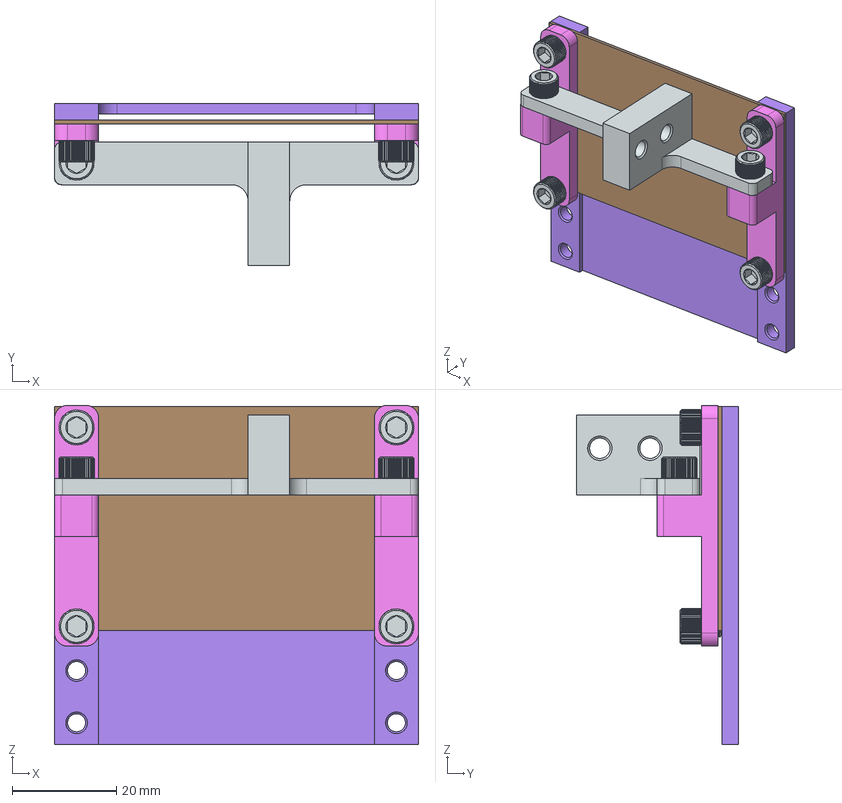
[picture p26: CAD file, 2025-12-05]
Final Fabrication Package/CAD/ASSEM_Horizontal Actuation Assembly.stp
70.0 x 31.1 x 65.3 mm
Horizontal Mount
Mesh Clamp x 2
Film Plate
6_32 UNC 1_2in 18_8 Screw 92196A190 x 6

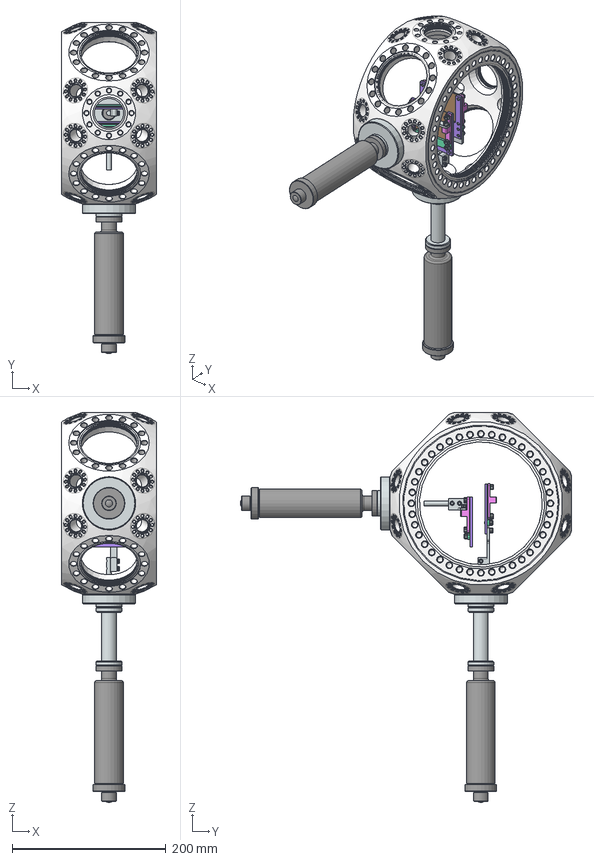
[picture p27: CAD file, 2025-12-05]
Final Fabrication Package/CAD/ASSEM_Full Film Bending Assembly.stp
124.0 x 431.5 x 507.7 mm
Vacuum Chamber
CF 1_33 to CF 2_75 Adapter x 2
T_Bar
MDC Linear Passthrough x 2
Horizontal Mount
Mesh Clamp x 4
Film Plate x 2
Film Clamp x 2
Horizontal Actuator Tip
6_32 UNC 1_2in 18_8 Screw 92196A190 x 16
8_32 UNC 1_4in 18_8 Screw 92196A148 x 4
Vertical Mount
Vertical Actuator Tip

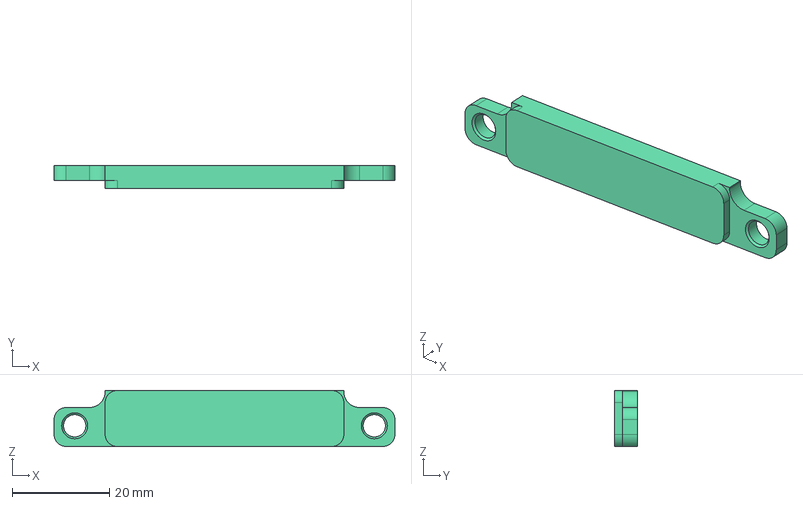
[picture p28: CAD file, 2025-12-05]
Final Fabrication Package/CAD/Film Clamp.stp
70.0 x 4.76 x 11.5 mm

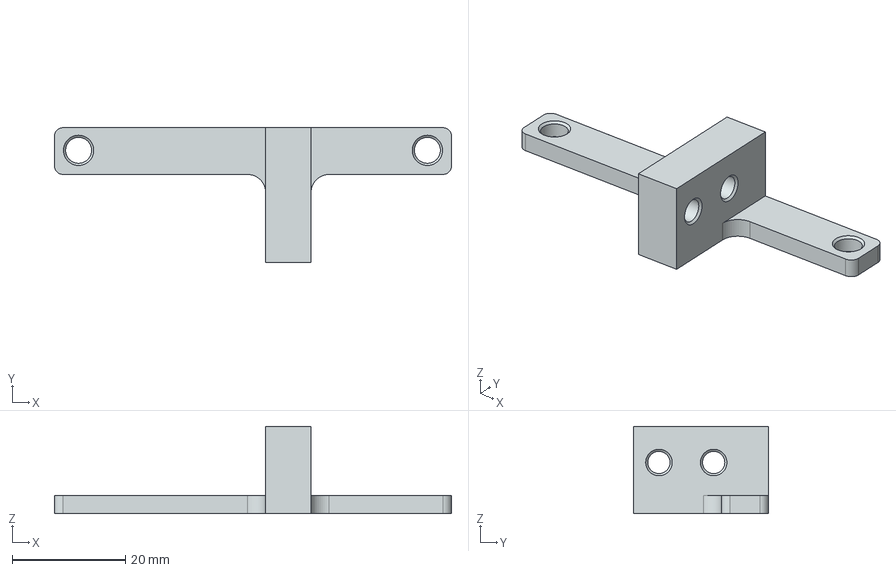
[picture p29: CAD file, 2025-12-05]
Final Fabrication Package/CAD/Horizontal Mount.stp
70.0 x 23.8 x 15.4 mm

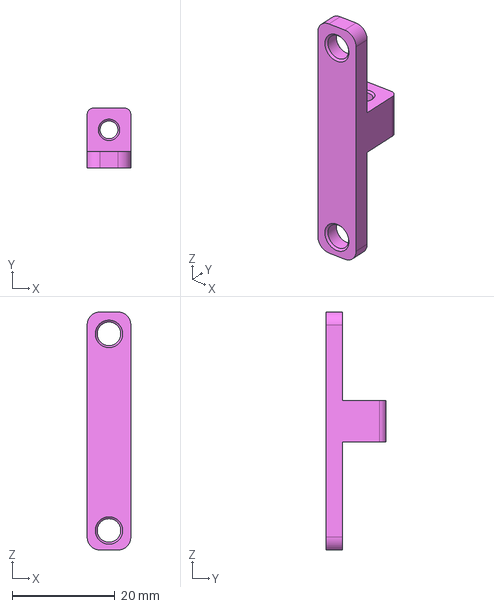
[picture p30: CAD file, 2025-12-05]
Final Fabrication Package/CAD/Mesh Clamp.stp
8.50 x 11.7 x 46.3 mm

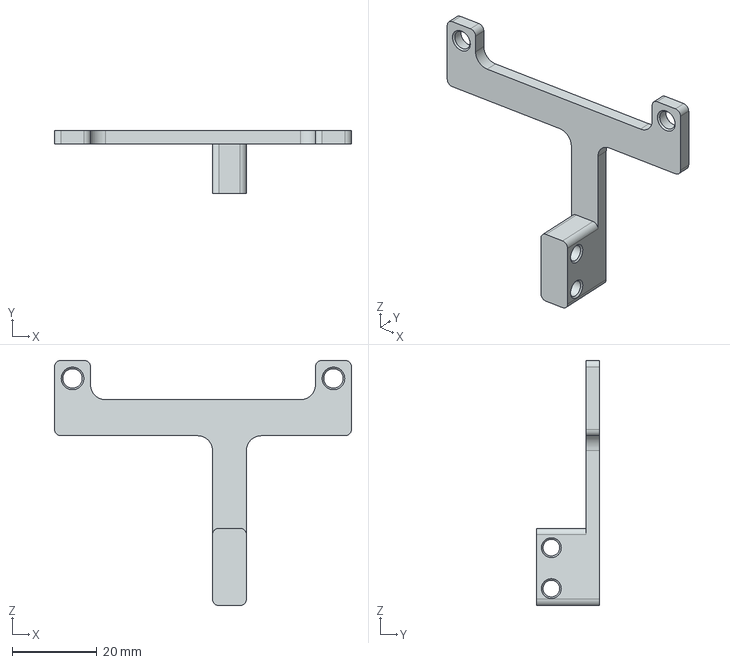
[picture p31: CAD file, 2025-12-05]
Final Fabrication Package/CAD/Vertical Mount.stp
70.0 x 14.8 x 57.8 mm

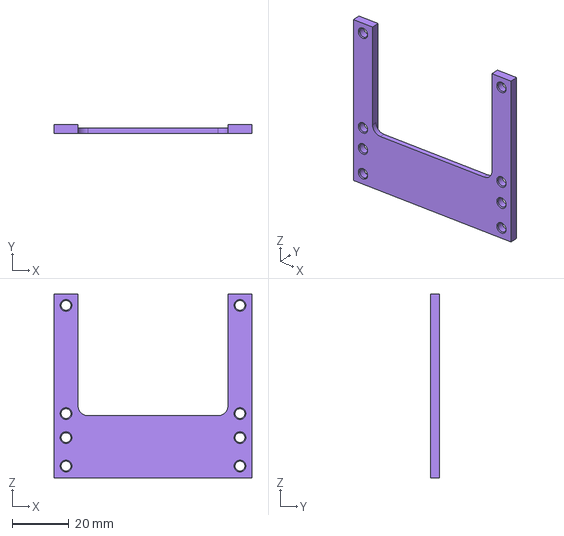
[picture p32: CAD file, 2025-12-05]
Final Fabrication Package/CAD/Film Plate.stp
70.0 x 3.18 x 65.0 mm

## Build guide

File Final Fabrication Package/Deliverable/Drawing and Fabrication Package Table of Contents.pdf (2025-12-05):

1

## Table of Contents

Table of Contents | 1
Bill of Materials | 2
Full Assembly | 3
Horizontal Actuation Assembly | 4
Vertical Mount | 5
Horizontal Mount | 6
Mesh Clamp | 7
Film Plate | 8
Film Clamp | 9

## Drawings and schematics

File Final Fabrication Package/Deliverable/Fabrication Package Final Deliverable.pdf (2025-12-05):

1

## Table of Contents

Table of Contents | 1
Bill of Materials | 2
Full Assembly | 3
Horizontal Actuation Assembly | 4
Vertical Mount | 5
Horizontal Mount | 6
Mesh Clamp | 7
Film Plate | 8
Film Clamp | 9

Item | Description | Link | Cost | Qty
#8-32 1/4" Stainless Steel Socket Head Screw | Plate Fastening Screws | https://www.mcmaster.com/92196A190 $ | | 1 7.21

## #6-32 1/2" Stainless Steel

Socket Head Screw | Linear Actuator Screws | https://www.mcmaster.com/92196A148 $ | 1 7.62

## MDC Precision Linear Motion

Feedthrough | Radius Adjustment Linear Actuator | https://www.mdcprecision.com/parts/linear-motion-feedthrough-133-flange-2-travel $ | 1 996.00 | *Already in lab
MDC Precision Linear Motion Feedthrough | Linear Sweeping Actuator | https://www.mdcprecision.com/parts/linear-motion-feedthrough-133-flange-2-travel ?? | 1 | *Need to select motorized option
2.75" Flange Adapter (Reduce to 1.33" CF) | Linear actuator flange adapter | https://www.kimballphysics.com/product/mcf275-flgadptr-c1a1/ $ | 2 288.00 | *At least one already in lab
| | PTFE-Coated Fiberglass Fabric Sheet, Mesh, 40" Wide | McMaster-Carr $ 34.33 | 1
Film Plate | TOBE MACHINED | Drawing in Fabrication Package | 2
Film Clamp | TOBE MACHINED | Drawing in Fabrication Package | 2
Mesh Clamp | TOBE MACHINED | Drawing in Fabrication Package | 4
Vertical Connector | TOBE MACHINED | Drawing in Fabrication Package | 1
Horizontal Connector | TOBE MACHINED | Drawing in Fabrication Package | 1

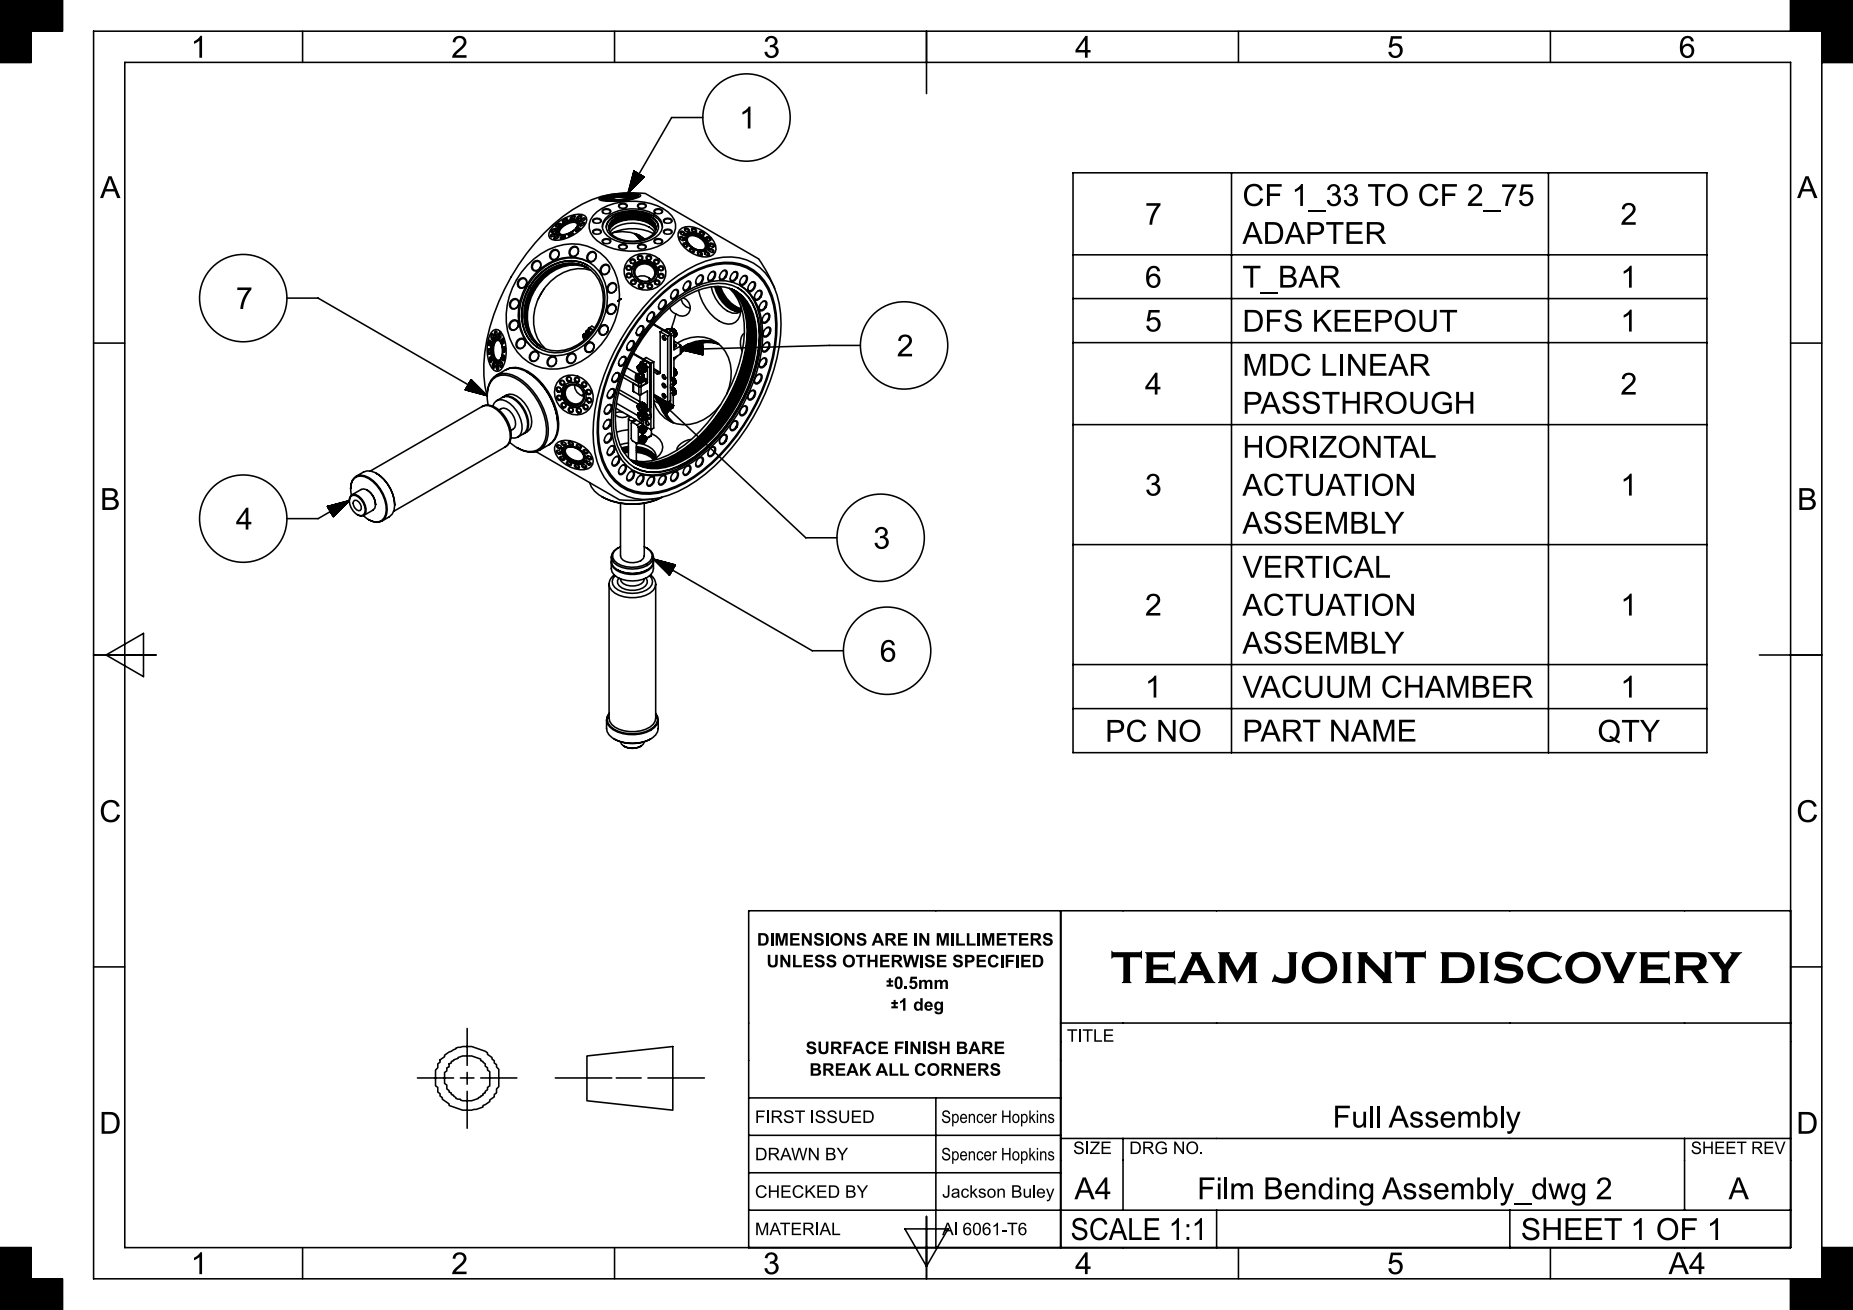
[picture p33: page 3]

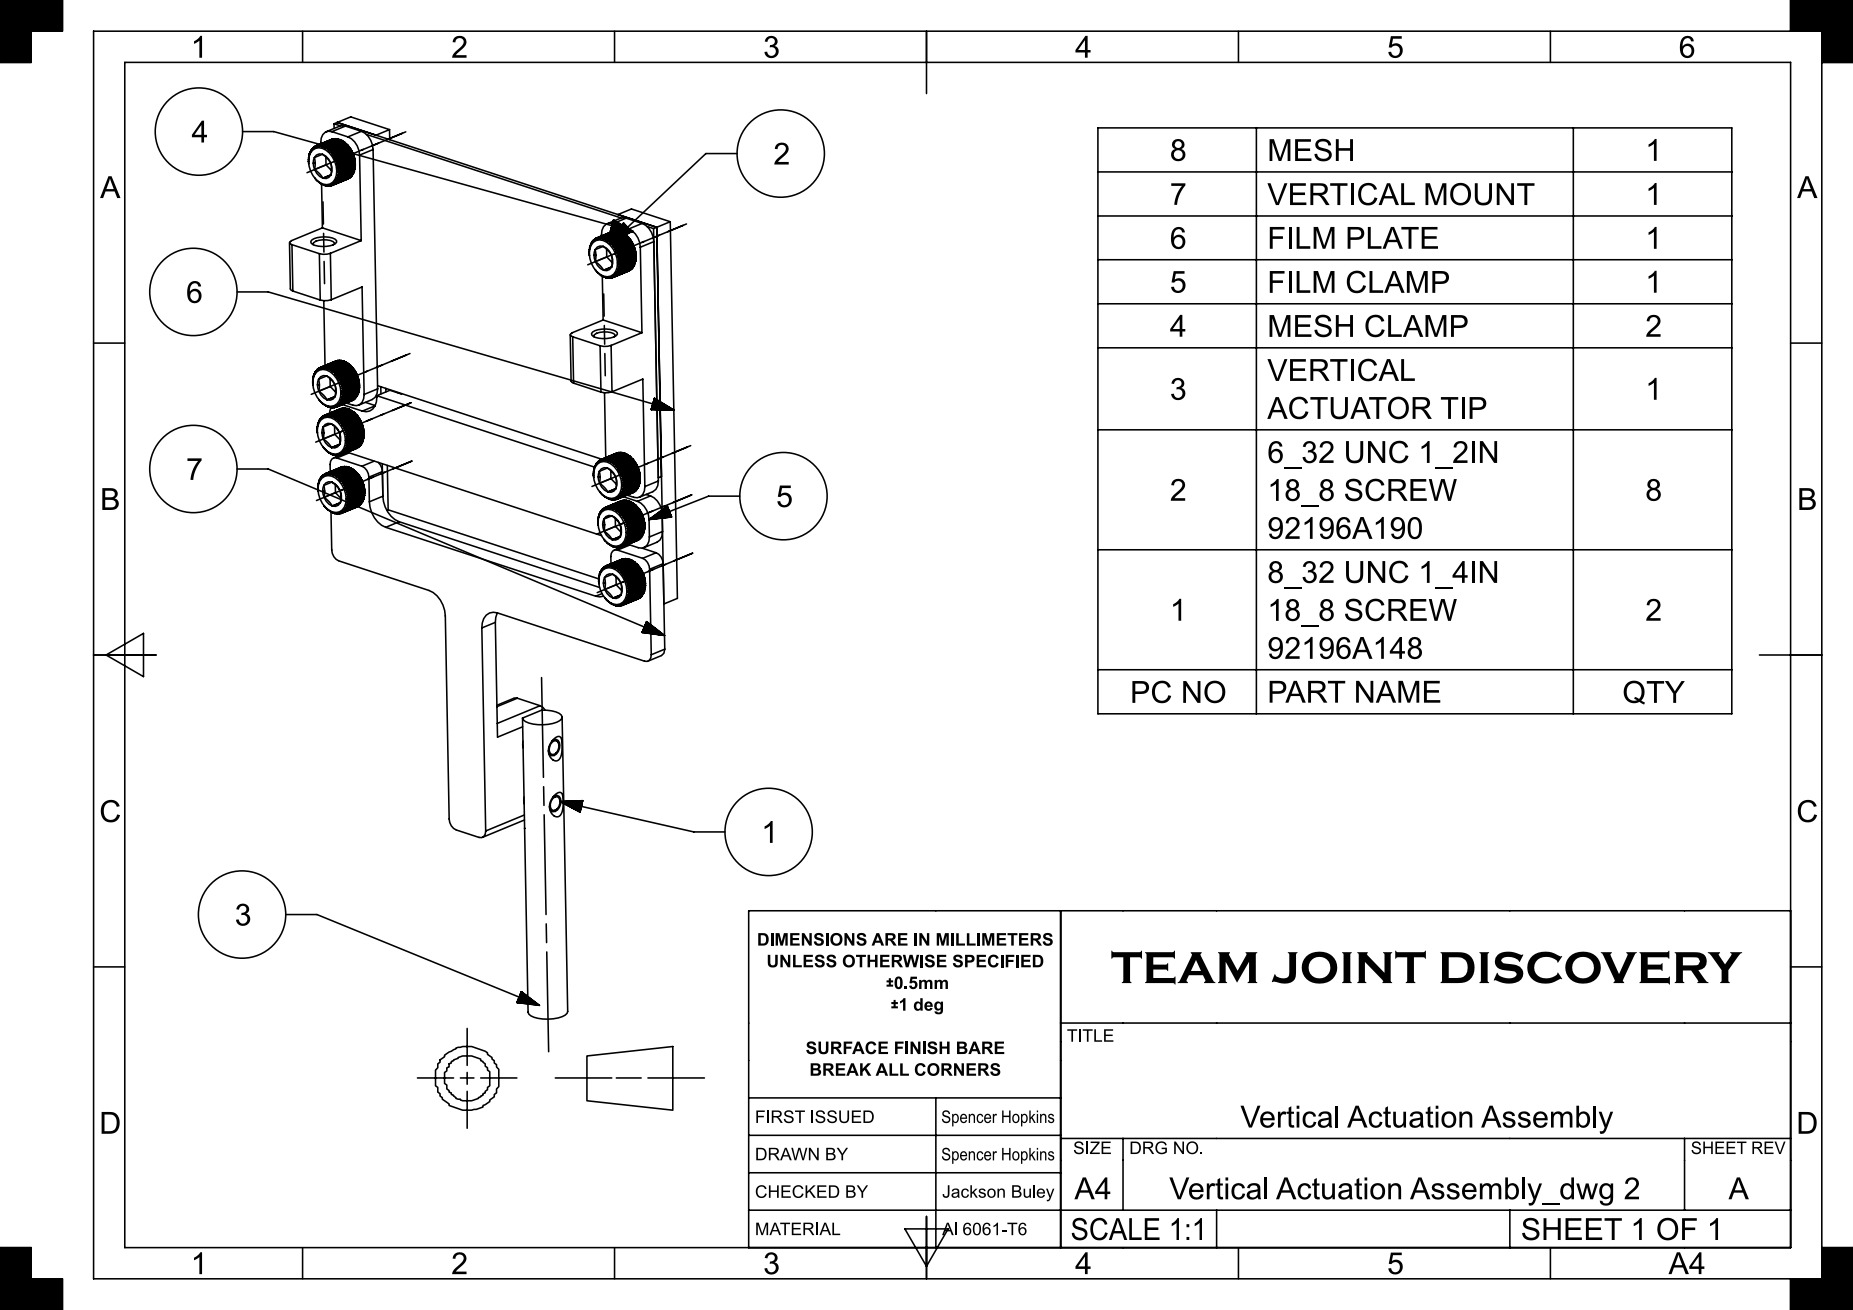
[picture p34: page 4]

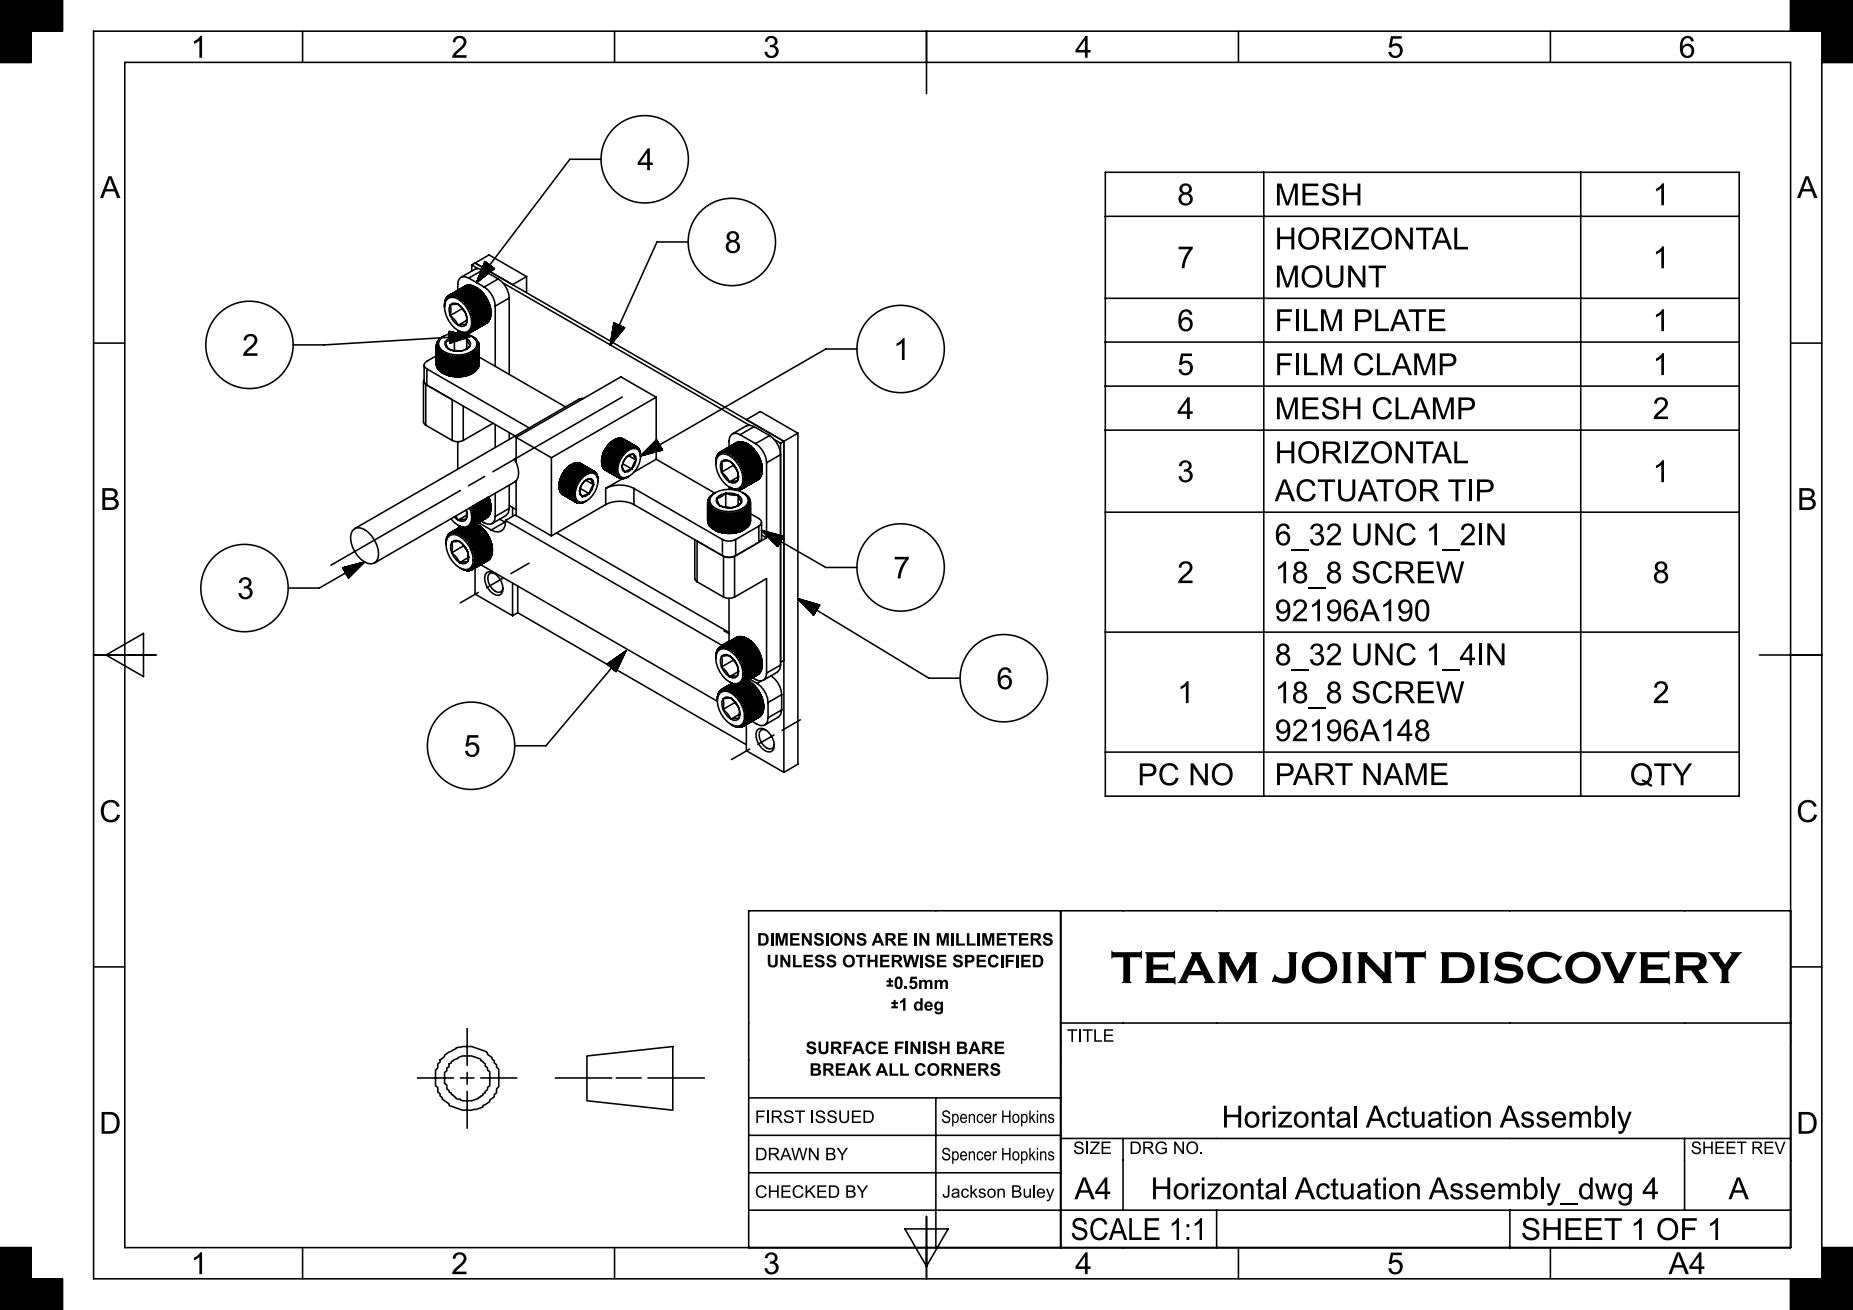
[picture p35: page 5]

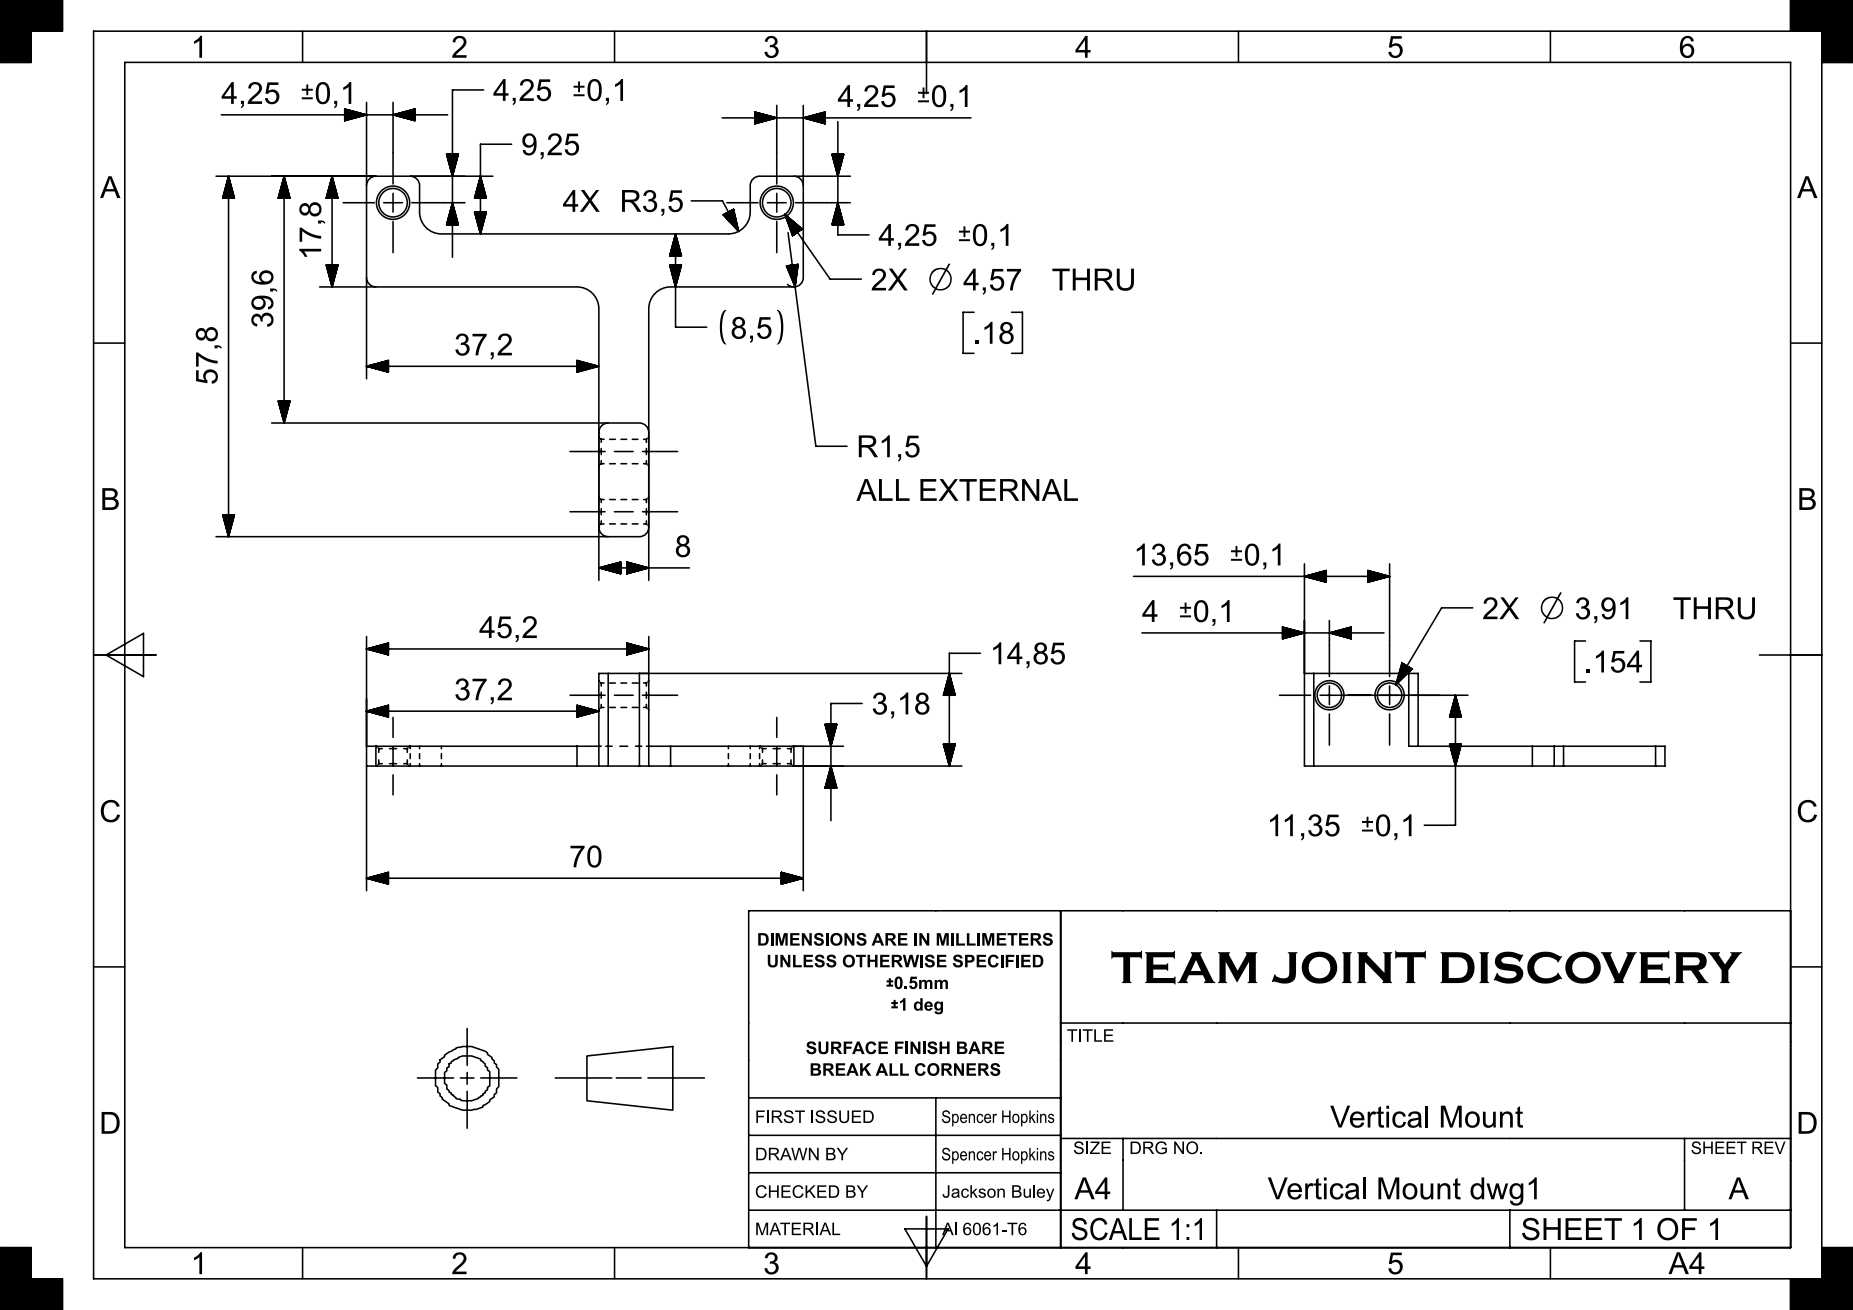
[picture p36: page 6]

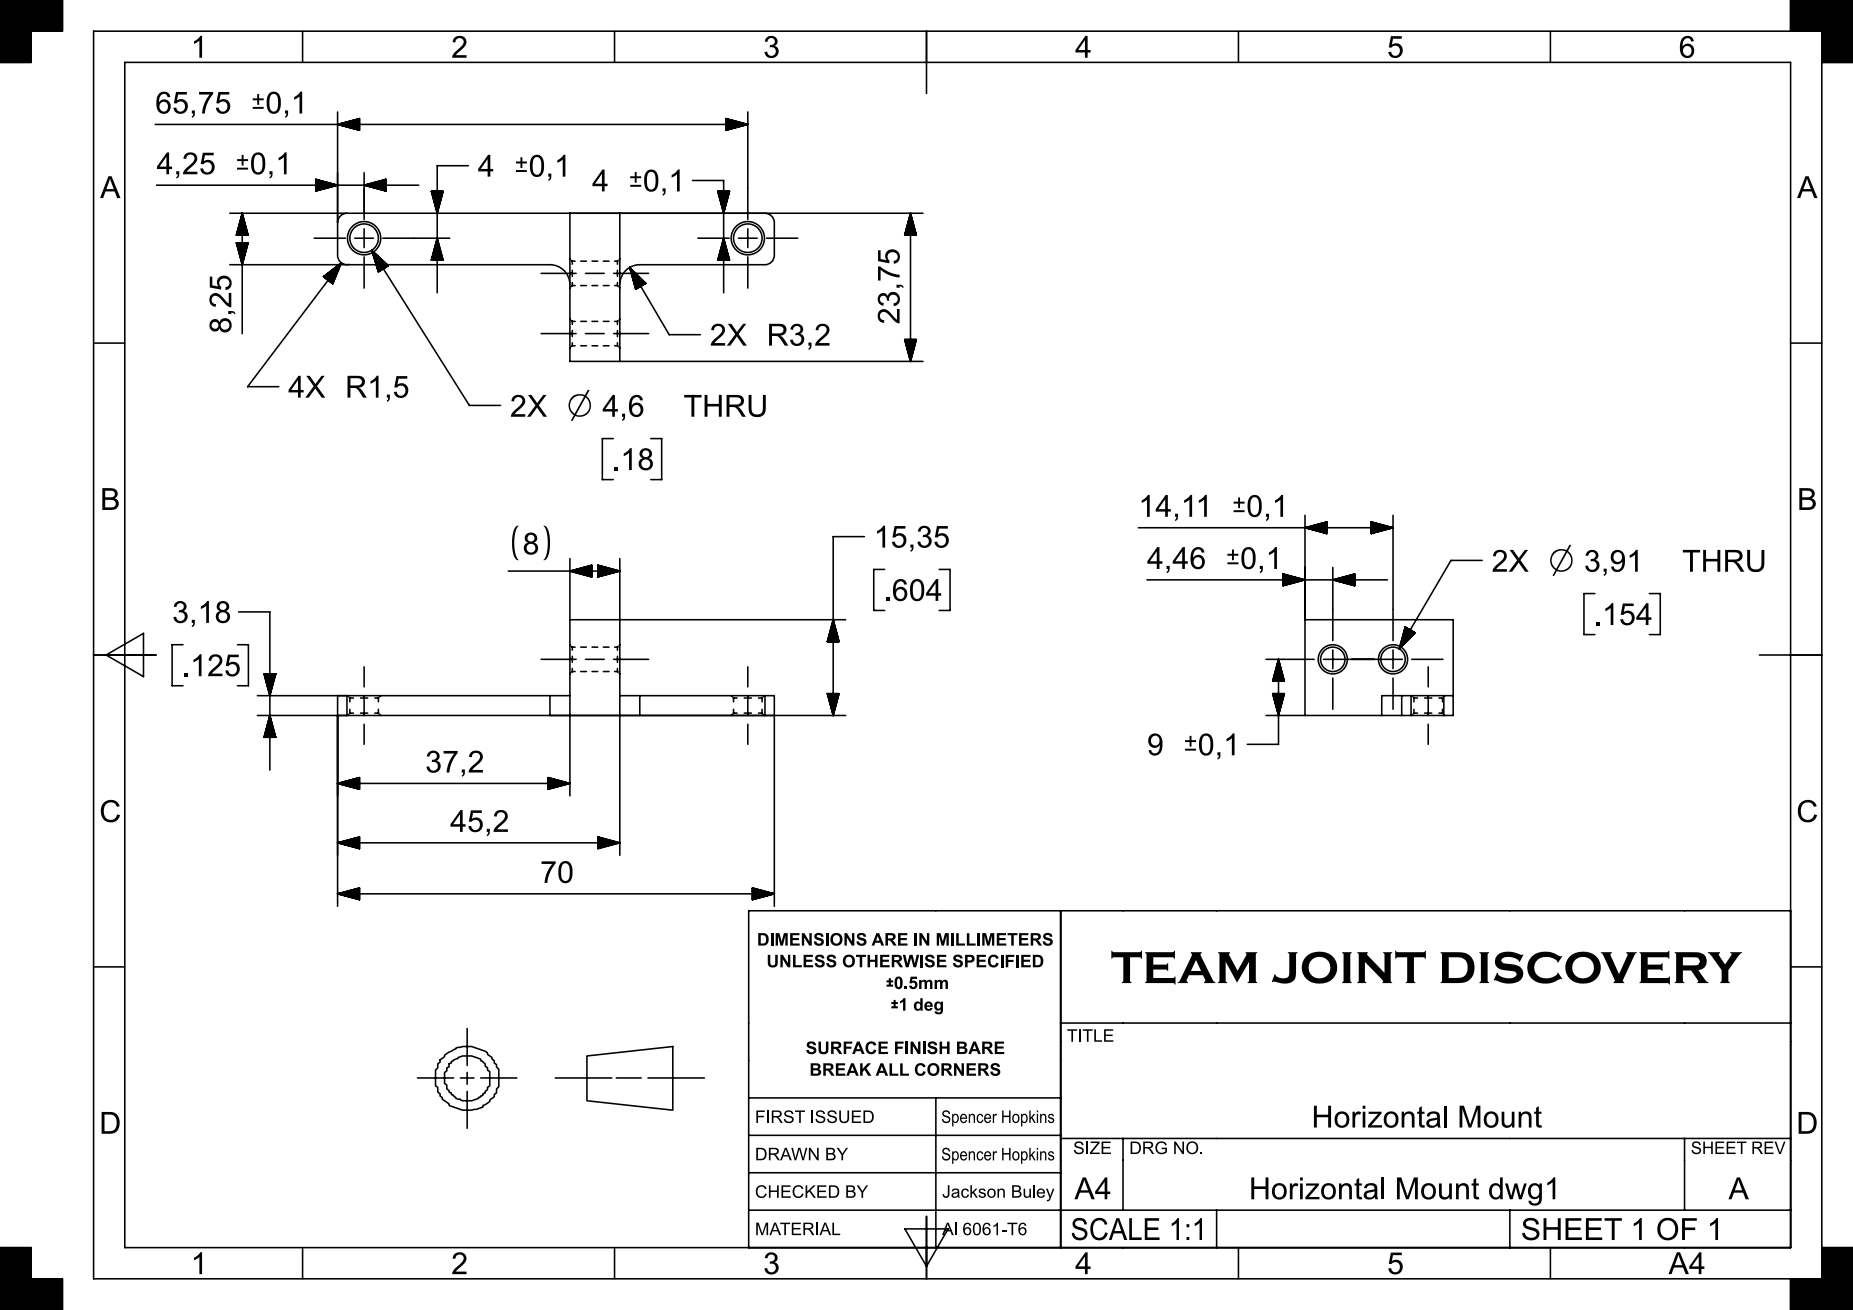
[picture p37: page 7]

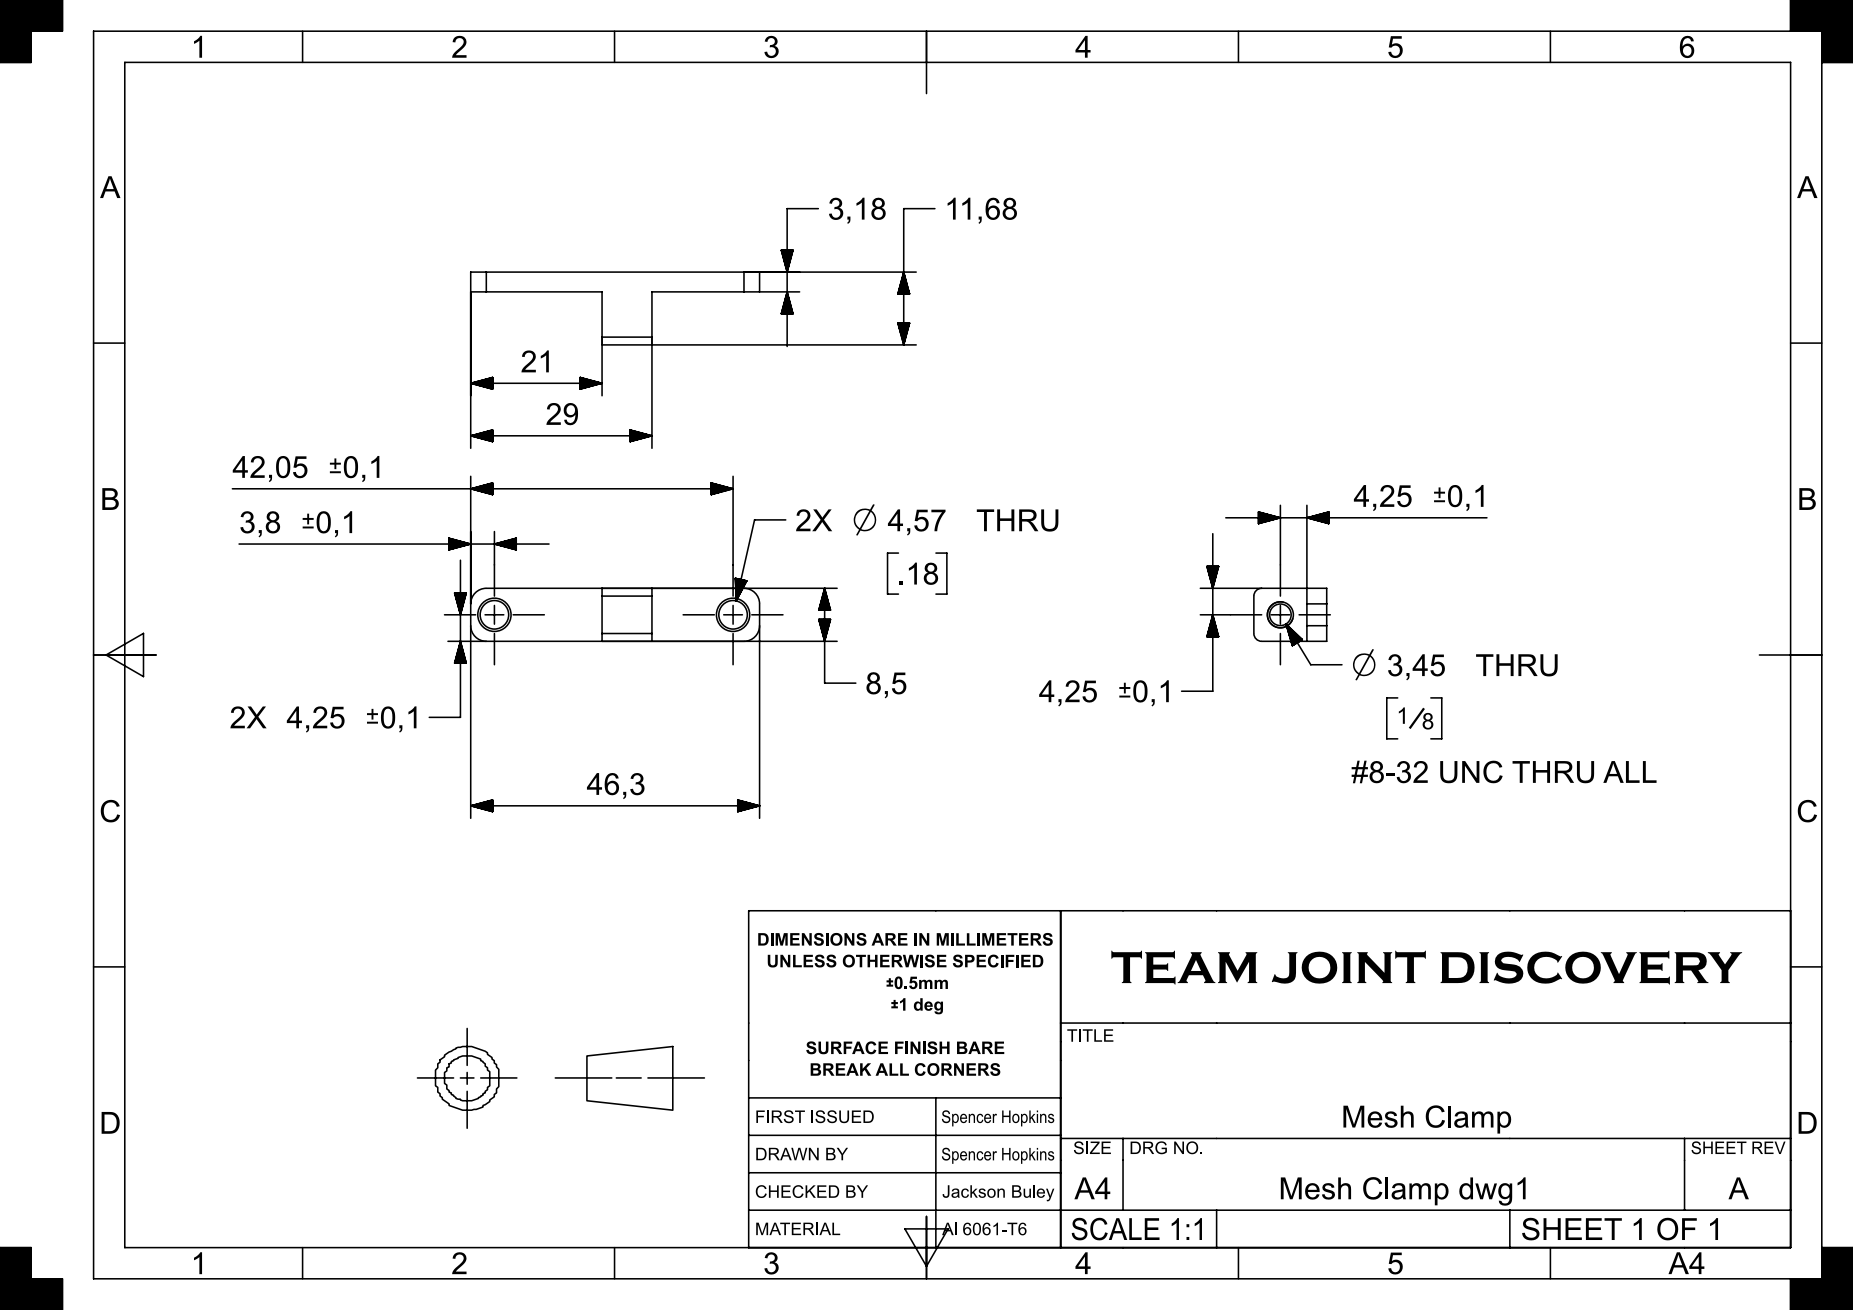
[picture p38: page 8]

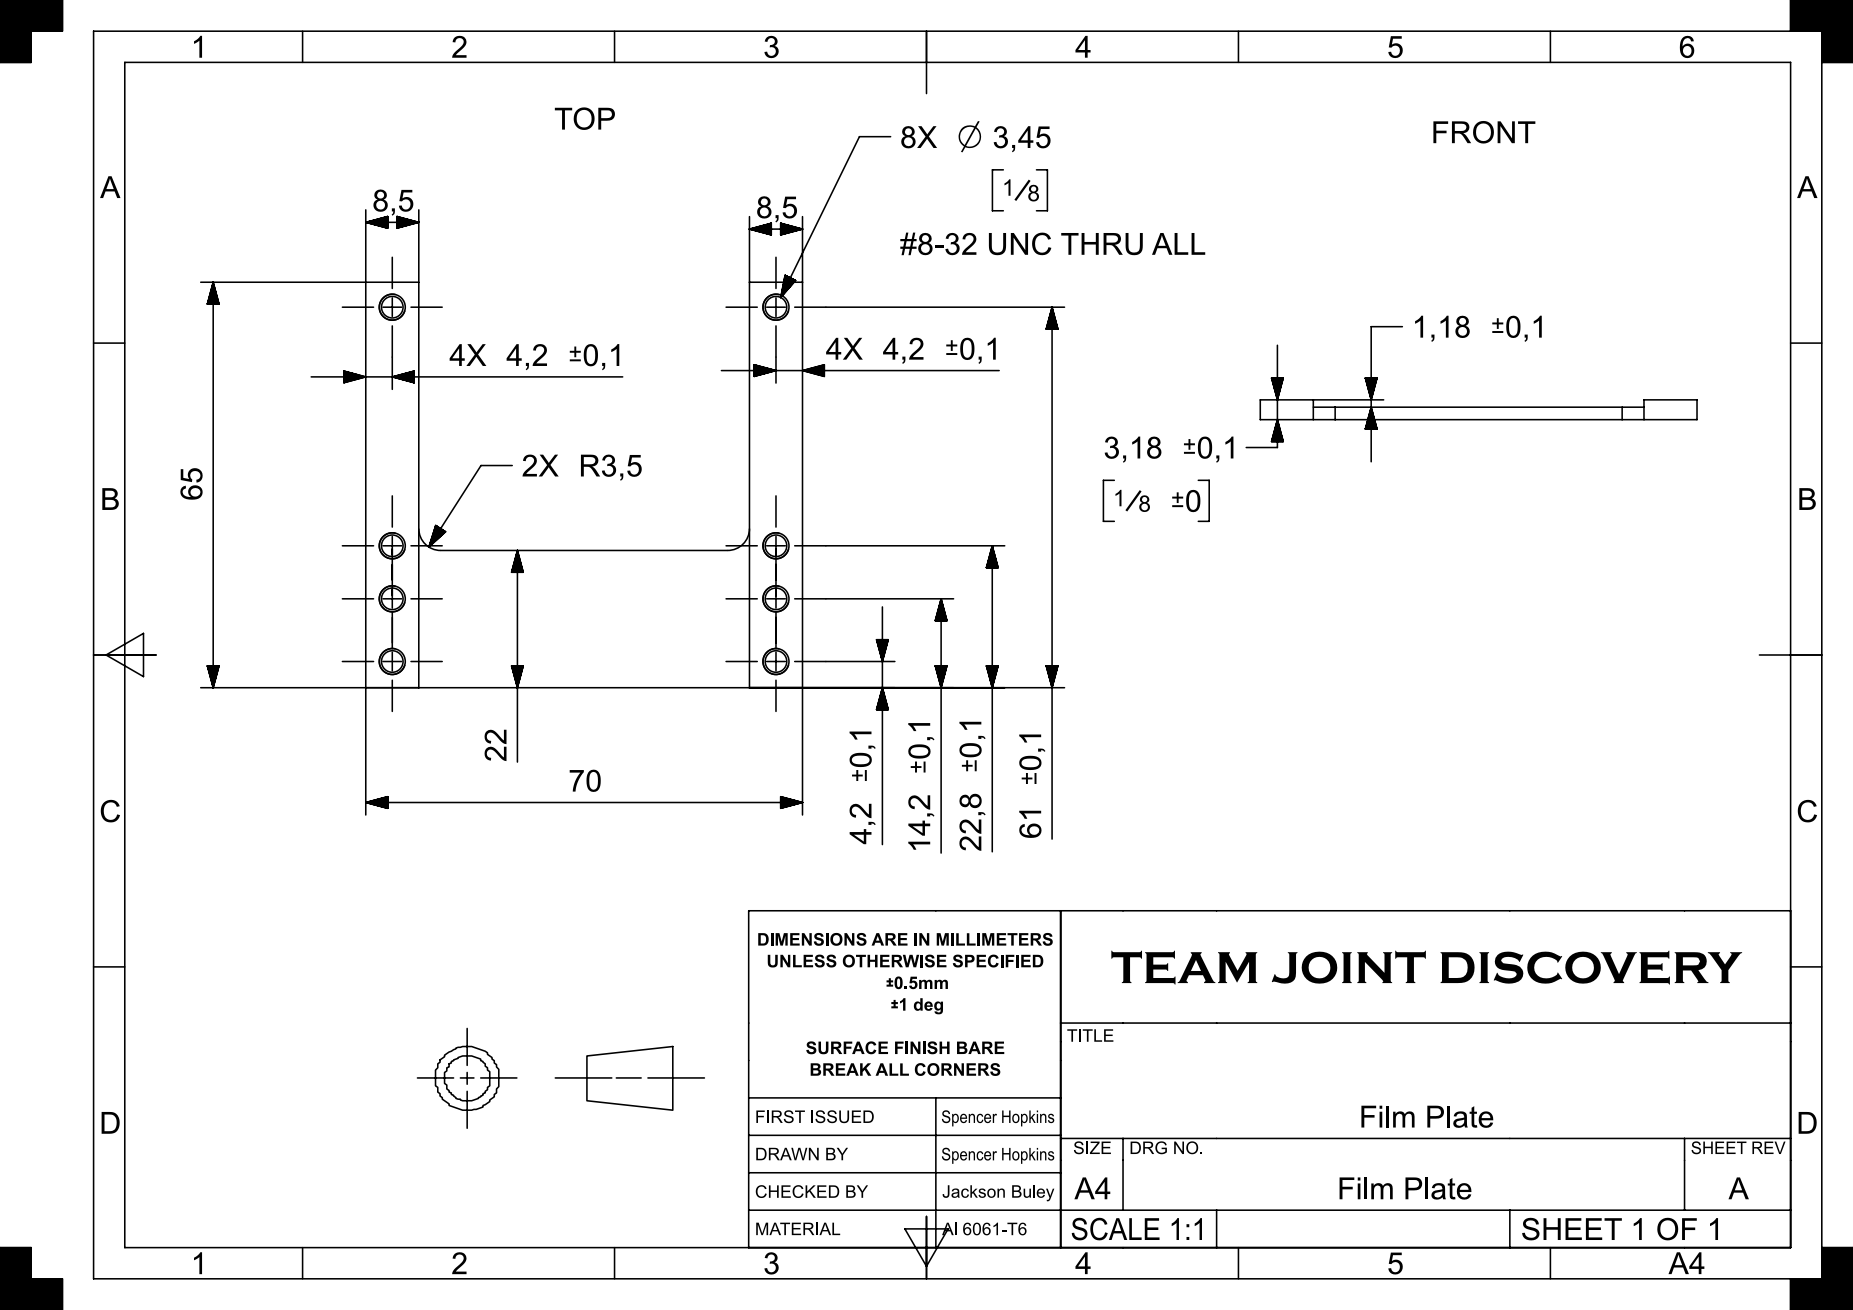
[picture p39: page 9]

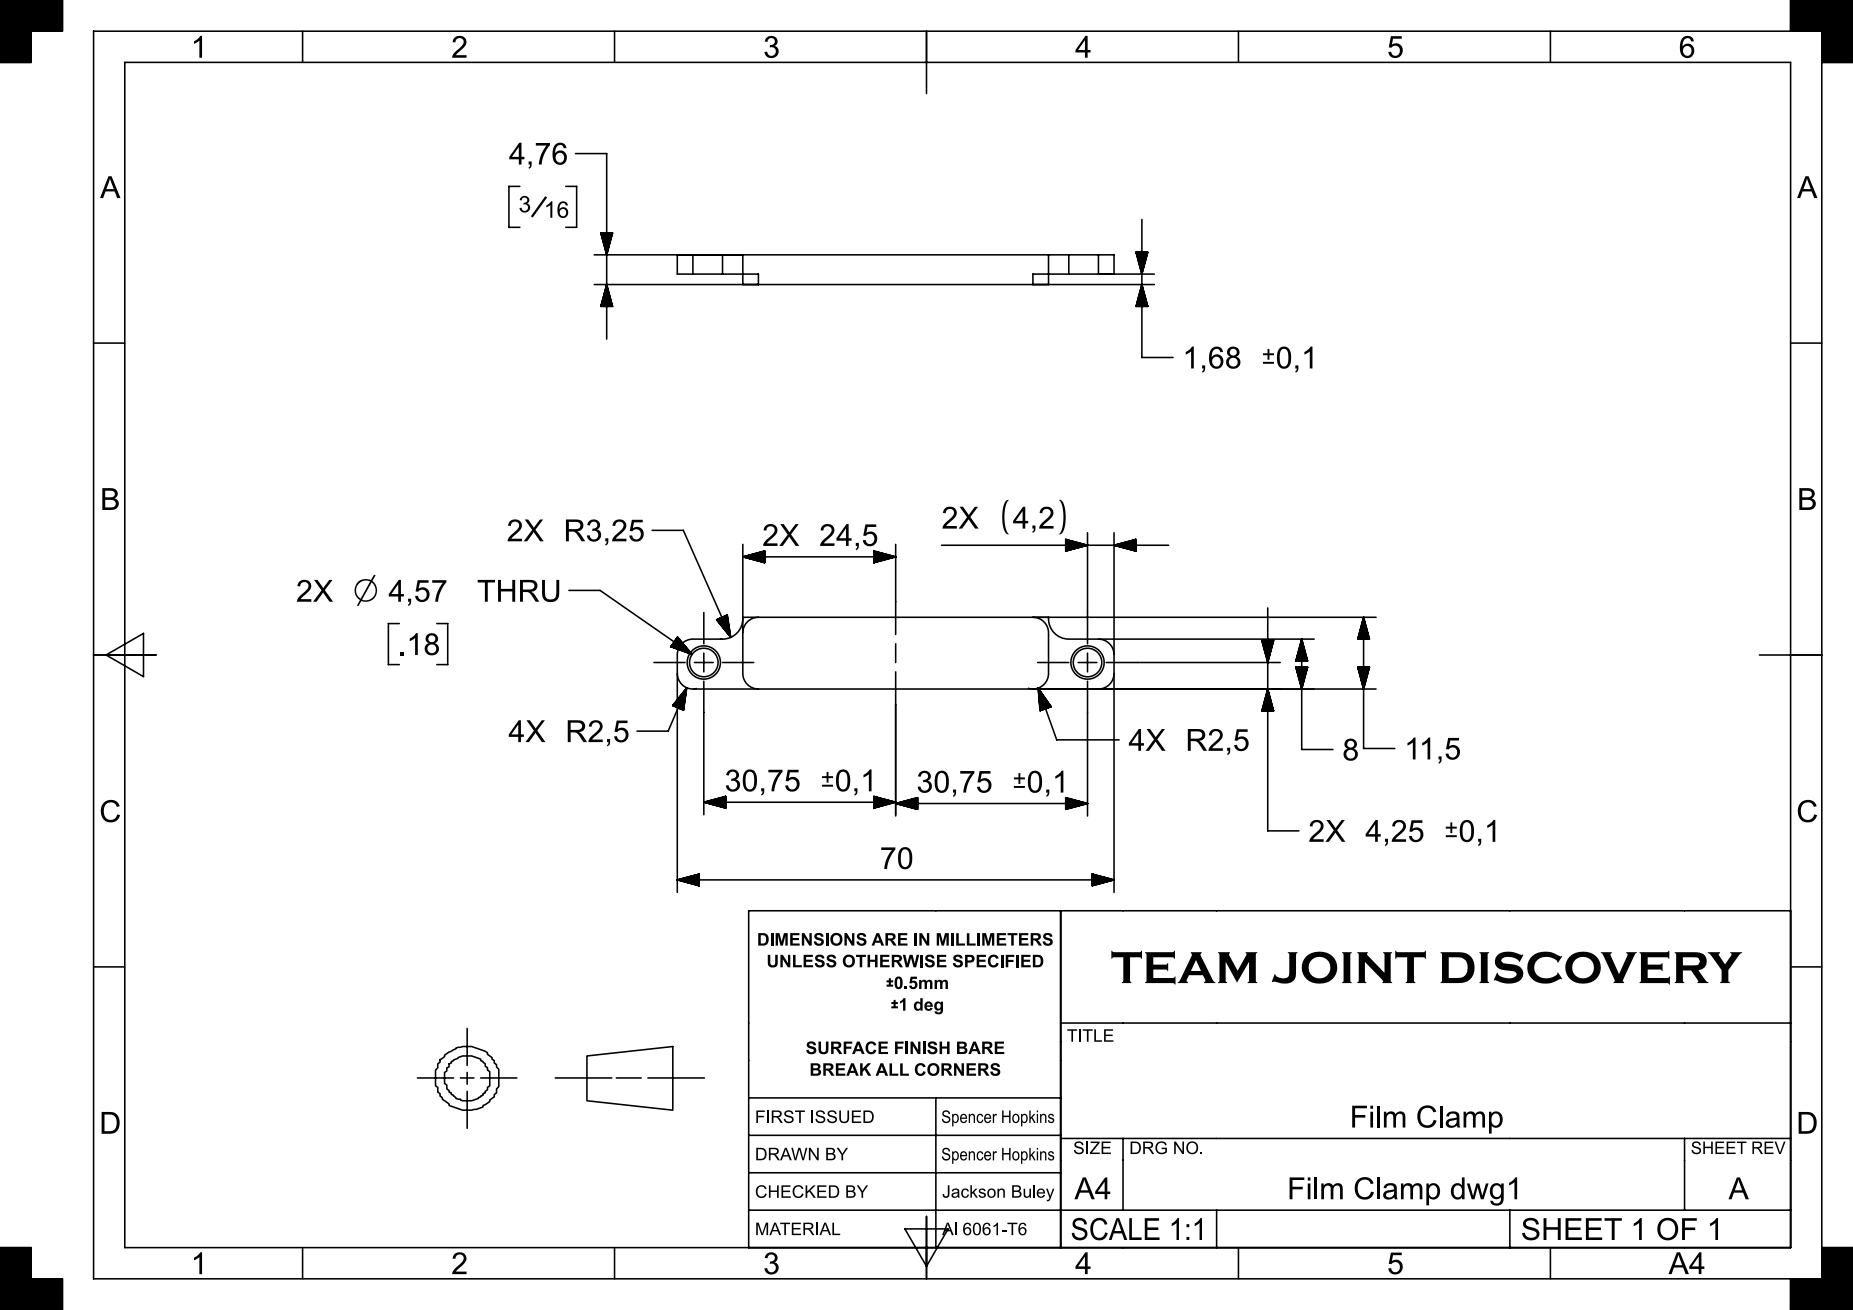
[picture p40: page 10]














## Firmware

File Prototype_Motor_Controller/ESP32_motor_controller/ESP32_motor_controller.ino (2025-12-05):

#include <AccelStepper.h>

#define HOMING false

// PIN DEFINITIONS
#define PIN_nENABLE     22
#define PIN_DIR          4
#define PIN_STEP        21
#define PIN_LIMIT_MIN   19
#define PIN_LIMIT_MAX   18

bool loopActive = false;
int loopTargetCount = 0;
int loopCount = 0;
long loopDistance = 0;
bool goingOut = true; 

// STEPPER SETUP
AccelStepper stepper(AccelStepper::DRIVER, PIN_STEP, PIN_DIR);

// positions
long targetPos = 0;
long maxPos = 0;

// settings
int maxSpeed = 400;
int accel = 400;

// serial buffer
String input = "";
String last_valid_command = "";

// status print interval
unsigned long lastStatusPrint = 0;
const unsigned long STATUS_INTERVAL = 100;  // ms

// SETUP
void setup() {
  Serial.begin(115200);
  Serial.println("nStepper Controller Booting");

  pinMode(PIN_nENABLE, OUTPUT);
  digitalWrite(PIN_nENABLE, LOW);

  pinMode(PIN_LIMIT_MIN, INPUT_PULLUP);
  pinMode(PIN_LIMIT_MAX, INPUT_PULLUP);

  stepper.setMaxSpeed(maxSpeed);
  stepper.setAcceleration(accel);

  if (HOMING) {
    Serial.println("Homing sequence starting...");
    homeAxis();
    Serial.println("Homing done.");
  } else {
    maxPos = 400000;
    stepper.setCurrentPosition(0);
  }
  digitalWrite(RGB_BUILTIN, HIGH);

  Serial.println("\nCommands:");
  Serial.println("  MOVE <steps>");
  Serial.println("  GOTO <position>");
  Serial.println("  SPEED <steps_per_sec>");
  Serial.println("  ZERO");
  Serial.println("======================================");
}

void loop() {

  if (Serial.available()) {
    char c = Serial.read();
    if (c == '\n') {
      Serial.printf("Received command: '%s'\n", input.c_str());
      processCommand(input);
      input = "";
    } else {
      input += c;
    }
  }

  //  enforce limits: MIN 
  if (digitalRead(PIN_LIMIT_MIN) == LOW) {
    if (stepper.currentPosition() != 0) {
      Serial.println("** MIN switch hit: position set to 0");
    }
    stepper.setCurrentPosition(0);

    if (stepper.targetPosition() < 0) {
      Serial.println("Clamped target to MIN");
      stepper.moveTo(0);
    }
  }

  //  enforce limits: MAX 
  if (digitalRead(PIN_LIMIT_MAX) == LOW) {
    if (stepper.currentPosition() != maxPos) {
      Serial.printf("** MAX switch hit: position set to %ld\n", maxPos);
    }
    stepper.setCurrentPosition(maxPos);

    if (stepper.targetPosition() > maxPos) {
      Serial.println("Clamped target to MAX");
      stepper.moveTo(maxPos);
    }
  }

  if (loopActive) {
      if (stepper.distanceToGo() == 0) {

          if (goingOut) {
              stepper.moveTo(loopDistance);
              goingOut = false;
              Serial.printf("Loop %d: Moving OUT → %ld\n", loopCount + 1, loopDistance);
          }

          // finished back to 0, loop finished
          else {
              stepper.moveTo(0);
              goingOut = true;
              loopCount++;

              Serial.printf("Loop %d: Returning BACK → 0\n", loopCount);

              if (loopCount >= loopTargetCount) {
                  loopActive = false;
                  Serial.println("LOOP COMPLETE.");
              }
          }
      }
  }

  // run stepper motion
  stepper.run();

  // print status
  unsigned long now = millis();
  if (now - lastStatusPrint >= STATUS_INTERVAL) {
    lastStatusPrint = now;

    Serial.printf(
      "[STATUS] Pos: %ld | Target: %ld | Speed: %.2f | Min: 0 | Max: %ld\n",
      stepper.currentPosition(),
      stepper.targetPosition(),
      stepper.speed(),
      maxPos
    );
  }
}




// homing
void homeAxis() {
  Serial.println("Homing: Searching for MIN...");
  rgbLedWrite(RGB_BUILTIN, 0, 0, 63);
  stepper.setMaxSpeed(300);
  stepper.setAcceleration(300);
  stepper.moveTo(-20000);

  while (digitalRead(PIN_LIMIT_MIN) != LOW) {
    stepper.run();
  }

  Serial.println("Homing: MIN switch triggered.");
  stepper.stop();
  delay(200);

  stepper.setCurrentPosition(0);  // set zero

  Serial.println("Homing: Searching for MAX...");
  rgbLedWrite(RGB_BUILTIN, 63, 63, 0);
  stepper.moveTo(20000);

  while (digitalRead(PIN_LIMIT_MAX) != LOW) {
    stepper.run();
  }

  Serial.println("Homing: MAX switch triggered.");
  stepper.stop();
  delay(200);

  maxPos = stepper.currentPosition();
  Serial.printf("Homing: Max travel = %ld steps\n", maxPos);

  long mid = maxPos / 2;
  Serial.printf("Homing: Moving to mid point: %ld\n", mid);
  stepper.moveTo(mid);

  while (stepper.distanceToGo() != 0) {
    stepper.run();
  }

  targetPos = mid;
  Serial.println("Homing: Midpoint reached");
}




// commands
void processCommand(String cmd) {
  cmd.trim();
  cmd.toUpperCase();

  // MOVE <steps>
  if (cmd.startsWith("MOVE")) {
    rgbLedWrite(RGB_BUILTIN, 0, 63, 0);
    long delta = cmd.substring(5).toInt();
    last_valid_command = "MOVE command: delta = " + String(delta);
    Serial.println(last_valid_command);

    long newTarget = targetPos + delta;
    if (newTarget < 0) newTarget = 0;
    if (newTarget > maxPos) newTarget = maxPos;

    targetPos = newTarget;
    Serial.printf("New target position: %ld\n", targetPos);
    stepper.moveTo(targetPos);
    return;
  }

  // GOTO <position>
  if (cmd.startsWith("GOTO")) {
    rgbLedWrite(RGB_BUILTIN, 63, 0, 63);
    long pos = cmd.substring(5).toInt();
    last_valid_command = "GOTO command: pos = " + String(pos);
    Serial.println(last_valid_command);

    if (pos < 0) pos = 0;
    if (pos > maxPos) pos = maxPos;

    targetPos = pos;
    Serial.printf("Clamped GOTO target: %ld\n", targetPos);
    stepper.moveTo(targetPos);
    return;
  }

  // SPEED <steps/sec>
  if (cmd.startsWith("SPEED")) {
    rgbLedWrite(RGB_BUILTIN, 20, 0, 0);
    maxSpeed = cmd.substring(6).toInt();
    stepper.setMaxSpeed(maxSpeed);

    last_valid_command = "Speed updated: " + String(maxSpeed);
    Serial.println(last_valid_command);
    return;
  }

  // ZERO
  if (cmd == "ZERO") {
    rgbLedWrite(RGB_BUILTIN, 0, 63, 63);
    stepper.setCurrentPosition(0);
    targetPos = 0;

    last_valid_command = "ZERO command: Position set to 0";
    Serial.println(last_valid_command);
    return;
  }

  if (cmd.startsWith("LOOP")) {
      int firstSpace = cmd.indexOf(' ');
      int secondSpace = cmd.indexOf(' ', firstSpace + 1);

      if (firstSpace < 0 || secondSpace < 0) {
        Serial.println("Usage: LOOP <count> <distance>");
        return;
      }

      loopTargetCount = cmd.substring(firstSpace + 1, secondSpace).toInt();
      loopDistance = cmd.substring(secondSpace + 1).toInt();

      loopCount = 0;
      goingOut = true;
      loopActive = true;

      Serial.printf("Starting LOOP: %d cycles, distance=%ld\n", loopTargetCount, loopDistance);

      // Start first outbound move
      stepper.moveTo(loopDistance);
      return;
  }


  // UNKNOWN
  Serial.println("Unknown command.");
  Serial.print("Last valid command: ");
  Serial.println(last_valid_command);
}

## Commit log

2025-12-05 Implement ESP32 motor controller with commands
    This code implements a motor controller for an ESP32 using the AccelStepper library. It includes setup for stepper motor control, limit switches, and command processing for movement and speed adjustm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
2025-12-05 Add ESP Motor Controller information to README
    Added section about ESP Motor Controller and usage notes.
2025-12-05 Uploaded Fabrication Package
    [ASSEM_Full Film Bending Assembly.stp, ASSEM_Horizontal Actuation Assembly.stp, ASSEM_Vertical Actuation Assembly.stp, BOM.xlsx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]
2025-12-05 folder reorg
    [Senior Design ESP32 Pinouts.xlsx]
2025-12-05 Updated fabrication package
    [BOM.xlsx]
